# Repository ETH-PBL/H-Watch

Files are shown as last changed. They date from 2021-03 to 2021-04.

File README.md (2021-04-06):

<!--
*** Template source: https://github.com/othneildrew/Best-README-Template/blob/master/README.md
-->

<!-- PROJECT SHIELDS -->
<!--
*** I'm using markdown "reference style" links for readability.
*** Reference links are enclosed in brackets [ ] instead of parentheses ( ).
*** See the bottom of this document for the declaration of the reference variables
*** for contributors-url, forks-url, etc. This is an optional, concise syntax you may use.
*** https://www.markdownguide.org/basic-syntax/#reference-style-links
-->
[][contributors-url]
[][forks-url]
[][stars-url]
[][issues-url]
[][license-url]

<!-- PROJECT LOGO -->
<br />
<p align="center">
  <a href="https://github.com/ETH-PBL/H-Watch">
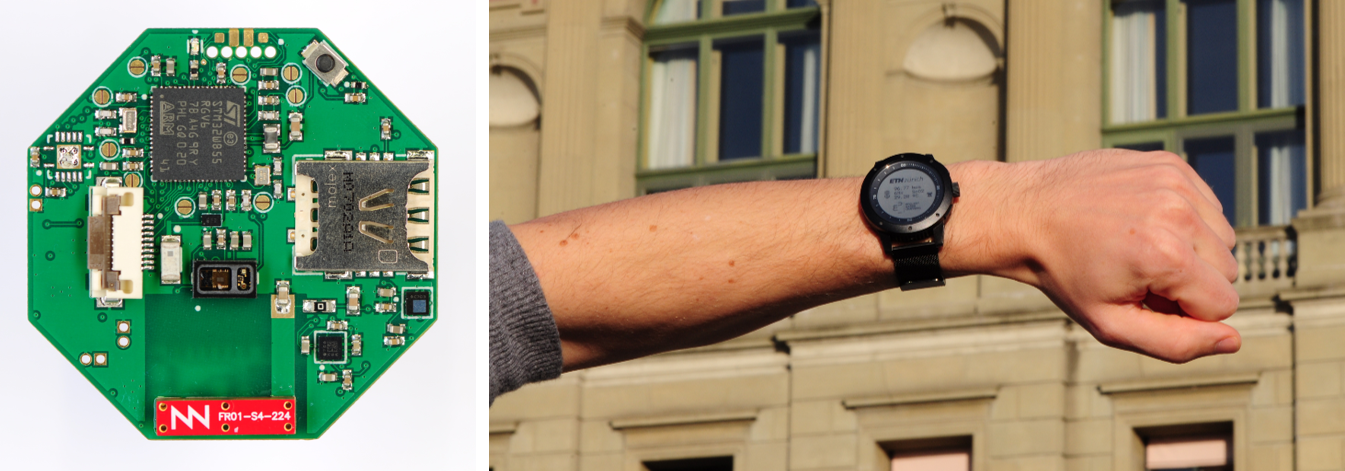
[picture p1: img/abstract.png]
    
  </a>

  <h3 align="center">H-Watch</h3>

  <p align="center">
    Smart Watch for Healthcare
    <br />
    <a href="https://github.com/ETH-PBL/H-Watch"><strong>Explore the docs »</strong></a>
    <br />
    <br />
    <a href="https://www.youtube.com/watch?v=JSp1-hzvBWk">View Demo</a>
    ·
    <a href="https://github.com/ETH-PBL/H-Watch/issues">Report Bug</a>
    ·
    <a href="https://github.com/ETH-PBL/H-Watch/issues">Request Feature</a>
  </p>
</p>

<!-- TABLE OF CONTENTS -->
## Table of Contents

* [About the Project](#about-the-project)
* [Hardware](#hardware)
  * [Components](#hardware)
  * [PCB](#pcb) 
* [Getting Started](#getting-started)
  * [Software](#software)
  * [Installation](#installation)

<!-- ABOUT THE PROJECT -->
## About The Project

The H-Watch is a fully open-sourde wearable long-lasting smart monitoring platform for health monitoring and tracking. Thanks to the integrated state-of-the-art NB-IoT cellular technology, it provides direct and secure cloud connectivity. It  is  based  on  widely  available  off-the-shelf components; however, it is designed with low-power and on-board intelligence in mind. Experimentalresults demonstrated only 5.9 mW of average power consumption, leading to a lifetime of 9 days on a small watch battery wothout, and up to 20 days with the solarenergy harvester.

## Hardware

### Components
The H-Watch is a highly integrated multi-sensor wearable platform which is built of the key components, listed below: 

* [MAX30101EFD+][max301010_url],  High-Sensitivity Pulse Oximeter and Heart-Rate Sensor for Wearable Health
* [LSM303AGR][lsm303agr_url],     Ultra-compact high-performance eCompass module
* [LPS22HB][lps22hb_url],         MEMS nano pressure sensor
* [LSM6DSM][lsm6dsm_url],         Ultra-low power, high accuracy and stability iNEMO 6DoF inertial measurement unit (IMU)
* [MP34DT05-A][mp34dt05_url],     MEMS audio sensor omnidirectional stereo digital microphone
* [BQ25570][bq25570_url],         Ultra Low power Harvester power Management IC with boost charger, and Nanopower Buck Converter
* [STM32WB55RG][stm32wb55_url],   Ultra-low-power dual core Arm Cortex-M4, Cortex-M0+ with 1 Mbyte of Flash memory, Bluetooth LE 5.2
* [BC95GJB-02-STD][bc95G_url],    Multi-band NB-IoT Module with Ultra-low Power Consumption

The H-Watchs housing, as well as its energy-saving memory LCD display, was taken from the [Matrix Power Watch][powerwatch_url] series 1.

### PCB 
The H-Watchs printed circuit board (PCB) is built of 6 Layers with a total board thichness of only 0.83mm. Further informations about the PCB can be found here:

File                                  | Content
--------------------------------------|--------
[H-Watch_schematics.pdf]              | Schematics of the H-Watch.  
[H-Watch_connectors.pdf]              | Description of the position and functionality of all connectors and test pionts.
[H-Watch_assembly.pdf]                | Assembly drawings of the top- and bottom-side of the PCB.
[H-Watch_manufacturing.pdf]           | Detailed fabrication information about the exansion board; thickness, dimensions and defined layer stack.
[H-Watch_layers.pdf]                  | Routing overview of all six copper layers.
[H-Watch_3D.pdf]                      | 3D model of the H-Watches hardware
[H-Watch_complete_documentation.pdf]  | The complete documentation contains all files above, excluding the 3D-PDF

The latest Altium files of of the PCB can be found [here][latest_altium_files]

<!-- GETTING STARTED -->

## Getting Started

* [STM32CubeIDE][stmcubeIDE_url]
* Firmware Package FW_WB V1.8.0

#### Software

### Installation

## Acknowledges
The authors recognise and thank the European Open Science Cloud (EOSC) for financial support under COVID-19 research to open access grant agreements.
EOSCsecretariat.eu has received funding from the European Union's Horizon Programme call H2020-INFRAEOSC-05-2018-2019, grant Agreement number 831644.

If you use **H-Watch** in an academic or industrial context, please cite the following publications:

~~~~
@INPROCEEDINGS{20.500.11850/476189,
	copyright = {Creative Commons Attribution 4.0 International},
	year = {2021-05-22},
	author = {Polonelli, Tommaso and Schulthess, Lukas and Mayer, Philipp and Magno, Michele and Benini, Luca},
	size = {6 p. submitted version},
	keywords = {wearable device; Covid-19; smart sensing; low power design; Tiny Machine Learning; wireless sensor networks},
	language = {en},
	DOI = {10.3929/ethz-b-000476189},
	title = {H-Watch: An Open, Connected Platform for AI-Enhanced COVID19 Infection Symptoms Monitoring and Contact Tracing.},
	Note = {IEEE International Symposium on Circuits and Systems (ISCAS 2021); Conference Location: online; Conference Date: May 22–28}
}
~~~~

<!-- MARKDOWN LINKS & IMAGES -->
<!-- https://www.markdownguide.org/basic-syntax/#reference-style-links -->

<!--Subsection Hardware-->
[max301010_url]:    https://www.maximintegrated.com/en/products/interface/sensor-interface/MAX30101.html
[lsm303agr_url]:    https://www.st.com/en/mems-and-sensors/lsm303agr.html
[lps22hb_url]:      https://www.st.com/en/mems-and-sensors/lps22hb.html
[lsm6dsm_url]:      https://www.st.com/en/mems-and-sensors/lsm6dsm.html
[mp34dt05_url]:     https://www.st.com/en/mems-and-sensors/mp34dt05-a.html
[bq25570_url]:      https://www.ti.com/product/BQ25570
[stm32wb55_url]:    https://www.st.com/en/microcontrollers-microprocessors/stm32wb55rg.html
[bc95G_url]:        https://www.quectel.com/UploadFile/Product/Quectel_BC95-G_NB-IoT_Specification_V1.2.pdf
[powerwatch_url]:   https://www.powerwatch.com/collections/powerwatch/products/black-ops-pack-10  

<!--Subsection PCB-->

[H-Watch_schematics.pdf]:                 /Hardware/H-Watch_V0.2/Documentation/H-Watch_schematics.PDF
[H-Watch_connectors.pdf]:                 /Hardware/H-Watch_V0.2/Documentation/H-Watch_connectors.PDF
[H-Watch_assembly.pdf]:                   /Hardware/H-Watch_V0.2/Documentation/H-Watch_assembly.PDF
[H-Watch_manufacturing.pdf]:              /Hardware/H-Watch_V0.2/Documentation/H-Watch_manufacturing.PDF
[H-Watch_layers.pdf]:                     /Hardware/H-Watch_V0.2/Documentation/H-Watch_layers.PDF
[H-Watch_3D.pdf]:                         /Hardware/H-Watch_V0.2/Documentation/H-Watch_3D.PDF
[H-Watch_complete_documentation.pdf]:     /Hardware/H-Watch_V0.2/Documentation/H-Watch_complete_documentation.PDF
[latest_altium_files]:                    /Hardware/H-Watch_V0.2/   

[stmcubeIDE_url]:	https://www.st.com/en/development-tools/stm32cubeide.html

[contributors-shield]: https://img.shields.io/github/contributors/ETH-PBL/H-Watch.svg?style=flat-square
[contributors-url]: https://github.com/ETH-PBL/H-Watch/graphs/contributors
[forks-shield]: https://img.shields.io/github/forks/ETH-PBL/H-Watch.svg?style=flat-square
[forks-url]: https://github.com/ETH-PBL/H-Watch/network/members
[stars-shield]: https://img.shields.io/github/stars/ETH-PBL/H-Watch.svg?style=flat-square
[stars-url]: https://github.com/ETH-PBL/H-Watch/stargazers
[issues-shield]: https://img.shields.io/github/issues/ETH-PBL/H-Watch.svg?style=flat-square
[issues-url]: https://github.com/ETH-PBL/H-Watch/issues
[license-shield]: https://img.shields.io/github/license/ETH-PBL/H-Watch.svg?style=flat-square
[license-url]: https://github.com/ETH-PBL/H-Watch/blob/master/LICENSE
[product-screenshot]: images/screenshot.png

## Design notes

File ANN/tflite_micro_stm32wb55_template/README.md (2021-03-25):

# STM32CubeIDE template project for STM32WB55 based on TensorFlow Lite micro.

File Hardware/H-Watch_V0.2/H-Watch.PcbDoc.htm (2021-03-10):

Reporting Options

# File in Newer Format

Date | : | 25/09/2020
Time | : | 15:45:50
Filename | : | C:\Users\tommy\OneDrive - Alma Mater Studiorum Università di Bologna\UniBo\SmartCOVID\PrimoPrototipo\SmartWatch\H-Watch.PcbDoc

Version | Warning
Release 20.0 | CAUTION - Support of propagation delay for primitives
Release 20.0 | CAUTION - Support for PCB system parameters, used to contain additional data extracted from components

This file was generated by a later version of the software

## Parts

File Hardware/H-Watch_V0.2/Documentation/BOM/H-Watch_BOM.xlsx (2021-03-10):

Quantity | Designator | Comment | Value | Tolerance | Power | Footprint | Manufacturer | Manufacturer Part Number
1 | R3 | 1M62 | 1620000.00 Ohm | 1 % | 0.1 W | RESC0603(1608)_L
1 | R4 | 7M32 | 7320000.00 Ohm | 1 % | 0.1 W | RESC0603(1608)_L
1 | R5 | 5M49 | 5490000.00 Ohm | 1 % | 0.1 W | RESC0603(1608)_L
2 | R6, R7 | 5M6 | 5600000.00 Ohm | 1 % | 0.1 W | RESC0603(1608)_L
2 | R8, R9 | 10K | 10000.00 Ohm | 1 % | 0.1 W | RESC0603(1608)_L
1 | C7 | 220n |  |  |  | CAPC1005X55X25ML05T10 | Murata
1 | D1 | SML-P11VTT86R |  |  |  | FP-SML-P1-MFG | Rohm | SML-P11VTT86R
1 | J1 | SOIC_Programmer |  |  |  | Programmer
1 | J2 | 52892-1033 |  |  |  | MOLX-52892-1033 | Molex
1 | J12 | 104224-0820 |  |  |  | 1042240820
1 | L1 | 2.2u |  | ±20% |  | INDC2013X140X50LL20T20 | Taiyo Yuden
1 | L2 | CBC3225T220MR | 22uH | 20% |  | INDC1210(3225)X27_L
1 | L3 | 1.5u |  | 20% |  | COILCRAFT-IND-LPS3015
1 | L4 | 6.8u |  | ±30% |  | SUMI-CDRH5D28_V | Sumida
1 | L5 | 10u |  |  |  | MURA-IND0805_L | Murata
1 | R1 | 30k |  |  |  | RESC1005X40X25ML05T05 | Panasonic
1 | R11 | 1.5k |  |  |  | RESC1005X40X25ML05T10 | Yageo / Phycomp
1 | R13 | 0R |  |  |  | RESC1609X55X30ML10T20 | Vishay Dale
1 | SW1 | B3U-1000P |  |  |  | OMRON-B3U-1000_V | Omron Electronic Components
1 | U1 | LSM303AGRTR |  |  |  | FP-LGA-12-8487206-MFG | STMicroelectronics | LSM303AGRTR
1 | U2 | MAX30101EFD+ |  |  |  | FP-F143A5-1-MFG | Maxim Integrated | MAX30101EFD+
1 | U3 | LPS22HBTR |  |  |  | FP-HLGA-10L-8479831-0 | STMicroelectronics | LPS22HBTR
1 | U4 | LSM6DSMTR |  |  |  | FP-LGA-14L-DM00249496-MFG | STMicroelectronics | LSM6DSMTR
1 | U5 | MP34DT05TR-A |  |  |  | FP-HCLGA-DM00231908-MFG | STMicroelectronics | MP34DT05TR-A
1 | U6 | TPS61096ADSST |  |  |  | SON50P200X80_HS-13N | Texas Instruments | TPS61096ADSST
1 | U7 | BQ25570RGRT |  |  |  | QFN50P350X350X100_HS-21L | Texas Instruments
1 | U8 | TPS63031DSKR |  |  |  | DSK10-2000X1200TP_V
1 | U9 | TPS62202DBVT |  |  |  | Z5+1_N
1 | U10 | LM3658SD |  |  |  | SDA10A | National Semiconductor
1 | U11 | STM32WB55RGV6 |  |  |  | FP-VFQFPN-68-B029-MFG | STMicroelectronics | STM32WB55RGV6
1 | U12 | AMCA31-2R450G-S1F-T3 |  |  |  | AMCA31
1 | U13 | MLPF-WB55-01E3 |  |  |  | MLPF-WB55-01E3
1 | U15 | BC95GJB-02-STD |  |  |  | BC95GJB-02-STD | Quectel Wireless Solutions | BC95GJB-02-STD
1 | U16 | FR01-S4-224 |  |  |  | FR01-S4-224 | Fractus Antennas S.L. | FR01-S4-224
1 | U17 | NUP3112UPMUTAG |  |  |  | ONSC-UDFN-6-517AP-01_V | On Semiconductor
1 | Y1 | ABS06-107-32.768KHZ-T |  |  |  | DFN140P200X60-2N-ABS06 | Abracon LLC | ABS06-107-32.768KHZ-T
1 | Y2 | ABM12-32.000MHZ-B2X-T3 |  | 20ppm |  | ABM12
2 | C21, C24 | CAP 4.7uF | 4.7uF | Â±10% |  | CAPC0603(1608)100_L
2 | C22, C25 | CAP 10nF | 10nF | Â±2% |  | CAPC0603(1608)100_L
2 | C32, C33 | CAP 1uF | 1uF | Â±10% |  | CAPC0603(1608)100_L
2 | C37, C38 | 4p |  |  |  | CAPC1005X55X25ML05T10 | Murata
2 | C40, C41 | 8p |  |  |  | CAPC1005X55X25NL05T10 | Murata
2 | C51, C54 | 100p |  |  |  | CAPC1005X56X25ML10T15 | AVX Interconnect / Elco
2 | C57, C58 | NM |  | 10% |  | CAPC1608X90X35ML10T15 | Murata
3 | C20, C30, C39 | 4.7u |  | ±10% |  | CAPC1608X90X20ML10 | TDK
3 | C60, C61, C62 | 33p |  |  |  | CAPC1005X56X25ML10T15 | AVX Interconnect / Elco
3 | R2, R10, R12 | 10k |  | 1% |  | RESC1005X40X25LL05T05 | Panasonic
3 | R14, R15, R16 | 1k |  |  |  | RESC1005X40X25NL05T05 | Vishay Dale
3 | R17, R18, R19 | 22R |  |  |  | RESC1005X40X25LL05T05 | Panasonic
3 | X1, X2, X3 | GRPB012VWVN-RC |  |  |  | Pin Header, 1x2, TH | Sullins Connector Solutions | GRPB012VWVN-RC
5 | C23, C26, C28, C29, C31 | 10u |  |  |  | CAPC1608X90X35NL10T15 | Murata
9 | J3, J4, J5, J6, J7, J8, J9, J10, J11 | Solder Jumper | 1 |  |  | Small Solder Jumper
14 | C1, C3, C5, C8, C9, C10, C12, C14, C16, C18, C42, C44, C46, C48 | 10u |  | ±20% |  | CAPC1005X70X10NL05 | TDK
22 | C2, C4, C6, C11, C13, C15, C17, C19, C27, C34, C35, C36, C43, C45, C47, C49, C50, C52, C53, C55, C56, C59 | 100n |  |  |  | CAPC1005X60X30ML05T10 | Kemet

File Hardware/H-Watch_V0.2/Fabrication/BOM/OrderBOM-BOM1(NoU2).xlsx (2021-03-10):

Name | Description | Designator | Quantity | Manufacturer 1 | Manufacturer Part Number 1 | Manufacturer Lifecycle 1 | Supplier 1 | Supplier Part Number 1 | Supplier Unit Price 1 | Supplier Subtotal 1
BC95GJB-02-STD | NB-IoT Module 54Kbps UART 700MHz to 2100MHz 3.6V Surface Mount | U15 | 1 | Quectel Wireless Solutions | BC95GJB-02-STD | Unknown
SOIC_Programmer |  | J1 | 1
LPS3015-152MRB | INDUCTOR, SHLD, 1.5UH, 20%, 1.3A, SMD | L3 | 1 | Coilcraft | LPS3015-152MRC | Unknown | Coilcraft Direct | LPS3015-152MRC | 0.85971 | 0.85971
5M49 1% 0603(1608) | 5M49 0.1W 1% 0603 (1608 Metric) SMD | R5 | 1 | Vishay | CRCW06035M49FKEA | Volume Production | Digi-Key | 541-5.49MHDKR-ND | 0.0966 | 0.0966
04023A330JAT2A |  | C60, C61, C62 | 3 | Kyocera AVX | 04023A330JAT2A | Volume Production | Digi-Key | 478-12613-6-ND | 0.0966 | 0.28979
04025A101FAT2A. |  | C51, C54 | 2 | Kyocera AVX | 04025A101FAT2A | Volume Production | Digi-Key | 478-3658-6-ND | 0.18353 | 0.36707
104224-0820 | 6 Position Card Connector NANO SIM Surface Mount, Right Angle Gold | J12 | 1 | Molex | 1042240820 | Not Recommended for New Design | Digi-Key | WM23749DKR-ND | 1.27 | 1.27
AMCA31-2R450G-S1F-T3 | Antennas 2.45GHz BW 90dB + Gain -1 dBi avg. | U12 | 1 | Abracon | AMCA31-2R450G-S1F-T3 | Volume Production | Digi-Key | 535-14095-6-ND | 0.51196 | 0.51196
C0402C104K8PACTU |  | C2, C4, C6, C11, C13, C15, C17, C19, C27, C34, C35, C36, C43, C45, C47, C49, C50, C52, C53, C55, C56, C59 | 22 | KEMET | C0402C104K8PACTU | Volume Production | Digi-Key | 399-3027-6-ND | 0.04443 | 0.97756
C1608X5R1C475K080AC | CAP, Ceramic, 4.7 uF, +/- 10%, 16 V, -55 to 85 degC, 0603 (1608 Metric), RoHS, Tape and Reel | C20, C30, C39 | 3 | TDK | C1608X5R1C475K080AC | Volume Production | Digi-Key | 445-7478-6-ND | 0.31877 | 0.95631
CAP 1uF 10V 0603(1608) | CAP 1uF 10V ±10% 0603 (1608 Metric) Thickness 1mm SMD | C32, C33 | 2 | KEMET | C0603C105K8RACTU | Volume Production | Digi-Key | 399-11133-6-ND | 0.0966 | 0.19319
CRCW06030000Z0EA |  | R13 | 1 | Vishay | CRCW0603-0000Z0EA | Volume Production | Digi-Key | 541-0.0GDKR-ND | 0 | 0
ERJ2RKF1002X | Chip Resistor, 10 KOhm, +/- 1%, 0.1 W, -55 to 155 degC, 0402 (1005 Metric), RoHS, Tape and Reel | R2, R10, R12 | 3 | Panasonic | ERJ-2RKF1002X | Volume Production | Digi-Key | P10.0KLDKR-ND | 0.0966 | 0.28979
FR01-S4-224 | 700MHz, 800MHz, 850MHz, 900MHz, 1.7GHz, 1.8GHz, 1.9GHz, 2GHz, 2.1GHz, 2.3GHz, 2.5GHz, 2.6GHz, 3.5GHz, 3.7GHz DCS, GSM, LTE, PCS, UMTS Chip RF Antenna 698MHz ~ 960MHz, 1.71GHz ~ 2.69GHz, 3.4GHz ~ 3.8GHz 1.6dBi, 3.7dBi, 3.1dBi Solder Surface Mount | U16 | 1 | Fractus | FR01-S4-224 | Unknown | Digi-Key | 2115-FR01-S4-224DKR-ND | 2 | 2
GJM1555C1H4R0CB01D |  | C37, C38 | 2 | Murata | GJM1555C1H4R0CB01D | Volume Production | Digi-Key | 490-3098-6-ND | 0.11592 | 0.23183
GRM155R71C224KA12D | Chip Capacitor, 220 nF, +/- 10%, 16 V, -55 to 125 degC, 0402 (1005 Metric), RoHS, Tape and Reel | C7 | 1 | Murata | GRM155R71C224KA12D | Volume Production | Digi-Key | 490-5418-6-ND | 0.13524 | 0.13524
GRPB012VWVN-RC | CONN HEADER 1.27mm Pitch 1x2 POS TH DL PCB AU | X1, X2, X3 | 3 | Sullins | GRPB012VWVN-RC | Obsolete | Digi-Key | S9015E-01-ND | 0 | 0
MP34DT05TR-A | MEMS AUD MIC SENSOR OMNI 4HCLGA | U5 | 1 | STMicroelectronics | MP34DT05TR-A | Unknown | Digi-Key | 497-17809-1-ND | 1.28 | 1.28
NUP3112UPMUTAG | Quad Transient Voltage Suppressor Array, ESD Protection Diodes with Ultra-Low (0.7 pF) Capacitance, 6-Pin UDFN, Pb-Free, Tape and Reel | U17 | 1 | ON Semiconductor | NUP3112UPMUTAG | Volume Production | Digi-Key | NUP3112UPMUTAG-ND | 0.30124 | 903.71
RC0402FR-071K5L |  | R11 | 1 | Yageo | RC0402FR-071K5L | Volume Production | Digi-Key | 311-1.50KLRCT-ND | 0.0966 | 0.0966
STM32WB55RGV6 | ULTRA-LOW-POWER DUAL CORE ARM CO | U11 | 1 | STMicroelectronics | STM32WB55RGV6 | Unknown | Digi-Key | 497-18488-ND | 9.39 | 9.39
TXB0104RGYR | IC TRNSLTR BIDIRECTIONAL 14VQFN | U14 | 1 | Texas Instruments | TXB0104RGYR | Volume Production | Digi-Key | 296-21930-6-ND | 0.98529 | 0.98529
52892-1033 | 0.5 mm Pitch Easy-On(TM) Type FPC Connector, 2.0 mm Mated Height, Right Angle, ZIF, SMT, Bottom Contact, 10 Circuits, -40 to 85 degC, ELV and RoHS Compliant, Tape and Reel | J2 | 1 | Molex | 52892-1033 | Volume Production | Farnell | 2361316 | 0.62836 | 0.62836
C1005X5R0J106M050BC | Chip Capacitor, 10 uF, +/- 20%, -55 to 85 degC, 0402 (1005 Metric), RoHS, Tape and Reel | C1, C3, C5, C8, C9, C10, C12, C14, C16, C18, C42, C44, C46, C48 | 14 | TDK | C1005X5R0J106M050BC | Volume Production | Farnell | 2346872 | 1.11 | 15.51
GRM188R71H104KA93D | Chip Capacitor, 0.1 uF, +/- 10%, 50 V, -55 to 125 degC, 0603 (1608 Metric), RoHS, Tape and Reel | C57, C58 | 2 | Murata | GRM188R71H104KA93D | Volume Production | Farnell | 8820023 | 0.05431 | 0.54306
LM3658SD | Dual Source USB/AC Li Chemistry Charger IC for Portable Applications, 10-pin LLP | U10 | 1 | TI National Semiconductor | LM3658SD | Not Recommended for New Design | Farnell | 1312584 | 1.03 | 1.03
1M62 1% 0603(1608) | 1M62 0.1W 1% 0603 (1608 Metric) SMD | R3 | 1 | Vishay Dale | CRCW06031M62FKEB | Volume Production | Mouser | 71-CRCW06031M62FKEB | 0.0966 | 0.0966
5M6 1% 0603(1608) | 5M6 0.1W 1% 0603 (1608 Metric) SMD | R6, R7 | 2 | Vishay | CRCW06035M60FKEA | Volume Production | Mouser | 71-CRCW06035M60FKEA | 0.0966 | 0.19319
7M32 1% 0603(1608) | 7M32 0.1W 1% 0603 (1608 Metric) SMD | R4 | 1 | Vishay | CRCW06037M32FKEA | Not Recommended for New Design | Mouser | 71-CRCW06037M32FKEA | 0.0966 | 0.0966
10K 1% 0603(1608) | 10K 0.1W 1% 0603 (1608 Metric) SMD | R8, R9 | 2 | Bourns | CR0603-FX-1002ELF | Volume Production | Mouser | 652-CR0603FX-1002ELF | 0.00676 | 0.06762
ABM12-32.000MHZ-B2X-T3 | 32MHz ±20ppm Crystal 8pF 200 Ohm -20°C ~ 70°C Surface Mount 4-SMD, No Lead (DFN, LCC) | Y2 | 1 | Abracon | ABM12-32.000MHZ-B2X-T3 | Volume Production | Mouser | 815-ABM12-32-B2XT3 | 1.8 | 1.8
ABS06-107-32.768KHZ-T | CRYSTAL 32.7680KHZ 4PF SMD | Y1 | 1 | Abracon | ABS06-107-32.768KHZ-T | Volume Production | Mouser | 815-ABS06-107-32.7-T | 1.15 | 1.15
B3U-1000P | Ultra-Small Tactile Switch, 0.05 A, 12 V, -25 to 70 degC, 2-Pin SMD, RoHS, Tape and Reel | SW1 | 1 | Omron | B3U-1000P | Volume Production | Mouser | 653-B3U-1000P | 0.91767 | 0.91767
BRC2012T2R2MD | Wire-Wound Chip Power Inductor, 2.2 uH, +/- 20%, -40 to 105 degC, 2-Pin SMD (0805), RoHS, Tape and Reel | L1 | 1 | Taiyo Yuden | BRC2012T2R2MD | Volume Production | Mouser | 963-BRC2012T2R2MD | 0.32843 | 0.32843
CAP 4.7uF 10V 0603(1608) | CAP 4.7uF 10V ±10% 0603 (1608 Metric) Thickness 1mm SMD | C21, C24 | 2 | Yageo | CC0603KRX5R6BB475 | Volume Production | Mouser | 603-CC603KRX5R6BB475 | 0.22217 | 0.44435
CAP 10nF 10V 0603(1608) | CAP 10nF 10V ±2% 0603 (1608 Metric) Thickness 1mm SMD | C22, C25 | 2 | KEMET | C0603C103G8GACTU | Volume Production | Mouser | 80-C0603C103G8GACTU | 0.77278 | 1.55
CBC3225T220MR | FIXED IND 22UH 780MA 351 MOHM | L2 | 1 | Taiyo Yuden | CBC3225T220MR | Volume Production | Mouser | 963-CBC3225T220MR | 0.26081 | 0.26081
CDRH5D28NP-6R2NC | Power Inductor, 6.2 uH, +/- 30%, 1.8 A, -40 to 100 degC, 2-Pin SMD, RoHS, Tape and Reel | L4 | 1 | Sumida | CDRH5D28NP-6R2NC | Volume Production | Mouser | 851-CDRH5D28NP-6R2NC | 0.66652 | 0.66652
CRCW04021K00FKED |  | R14, R15, R16 | 3 | Vishay Dale | CRCW04021K00FKED | Volume Production | Mouser | 71-CRCW0402-1.0K-E3 | 0.0966 | 0.28979
ERJ2RKF22R0X |  | R17, R18, R19 | 3 | Panasonic | ERJ-2RKF22R0X | Volume Production | Mouser | 667-ERJ-2RKF22R0X | 0.0966 | 0.28979
ERJ-2RKF3002X |  | R1 | 1 | Panasonic | ERJ-2RKF3002X | Volume Production | Mouser | 667-ERJ-2RKF3002X | 0.0966 | 0.0966
GJM1555C1H8R0CB01D |  | C40, C41 | 2 | Murata | GJM1555C1H8R0CB01D | Volume Production | Mouser | 81-GJM1555C1H8R0CB01 | 0.11592 | 0.23183
GRM188R60J106ME47D |  | C23, C26, C28, C29, C31 | 5 | Murata | GRM188R60J106ME47D | Volume Production | Mouser | 81-GRM188R60J106ME47 | 0.35741 | 1.79
LPS22HBTR | MEMS NANO PRESSURE SENSOR: 260-1 | U3 | 1 | STMicroelectronics | LPS22HBTR | Volume Production | Mouser | 511-LPS22HBTR | 2.55 | 2.55
LQM21FN100M70L | Fixed Inductor, 10 uH, +/-20%, -55 to 125 degC, 2-Pin SMD (0805), RoHS, Tape and Reel | L5 | 1 | Murata | LQM21FN100M70L | Volume Production | Mouser | 81-LQM21FN100M70L | 0.19319 | 0.19319
LSM6DSMTR | IMU ACCEL/GYRO I2C/SPI 14LGA | U4 | 1 | STMicroelectronics | LSM6DSMTR | Not Recommended for New Design | Mouser | 511-LSM6DSMTR | 2.81 | 2.81
LSM303AGRTR | IMU ACCEL/MAG I2C/SPI 12LGA | U1 | 1 | STMicroelectronics | LSM303AGRTR | New Product | Mouser | 511-LSM303AGRTR | 2.56 | 2.56
MLPF-WB55-01E3 | Prices include import duty and tax. RF FILTER, 2.4GHZ TO 2.5GHZ, WLCSP-6; | U13 | 1 | STMicroelectronics | MLPF-WB55-01E3 | Unknown | Mouser | 511-MLPF-WB55-01E3 | 0.31877 | 0.31877
SML-P11VTT86R | LED RED CLEAR 1006 SMD | D1 | 1 | Rohm | SML-P11VTT86R | Volume Production | Mouser | 755-SML-P11VTT86R | 0.36707 | 0.36707
BQ25570RGRT | IC ENERGY HARV CTRLR BATT 20VQFN | U7 | 1 | Texas Instruments | BQ25570RGRT | Volume Production | TI store | BQ25570RGRT | 5.76 | 5.76
TPS61096ADSST | Boost Switching Regulator IC Positive Fixed 3.3V, - 2 Output 350mA (Switch) 6-WFDFN | U6 | 1 | Texas Instruments | TPS61096ADSST | Unknown | TI store | TPS61096ADSST | 1.75 | 1.75
TPS62202DBVT | Buck Switching Regulator IC Positive Fixed 1.8V 1 Output 300mA SOT-23 | U9 | 1 | Texas Instruments | TPS62202DBVR | Volume Production | TI store | TPS62202DBVR | 0.78244 | 0.78244
TPS63031DSKR | Buck-Boost Switching Regulator IC Positive Fixed 3.3V 1 Output 900mA (Switch) 10-WFDFN Exposed Pad | U8 | 1 | Texas Instruments | TPS63031DSKR | Volume Production | TI store | TPS63031DSKR | 1.37 | 1.37

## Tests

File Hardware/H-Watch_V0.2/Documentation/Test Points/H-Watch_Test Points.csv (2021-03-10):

Net | Name | X Coord | Y Coord | Side | Hole Size | Type

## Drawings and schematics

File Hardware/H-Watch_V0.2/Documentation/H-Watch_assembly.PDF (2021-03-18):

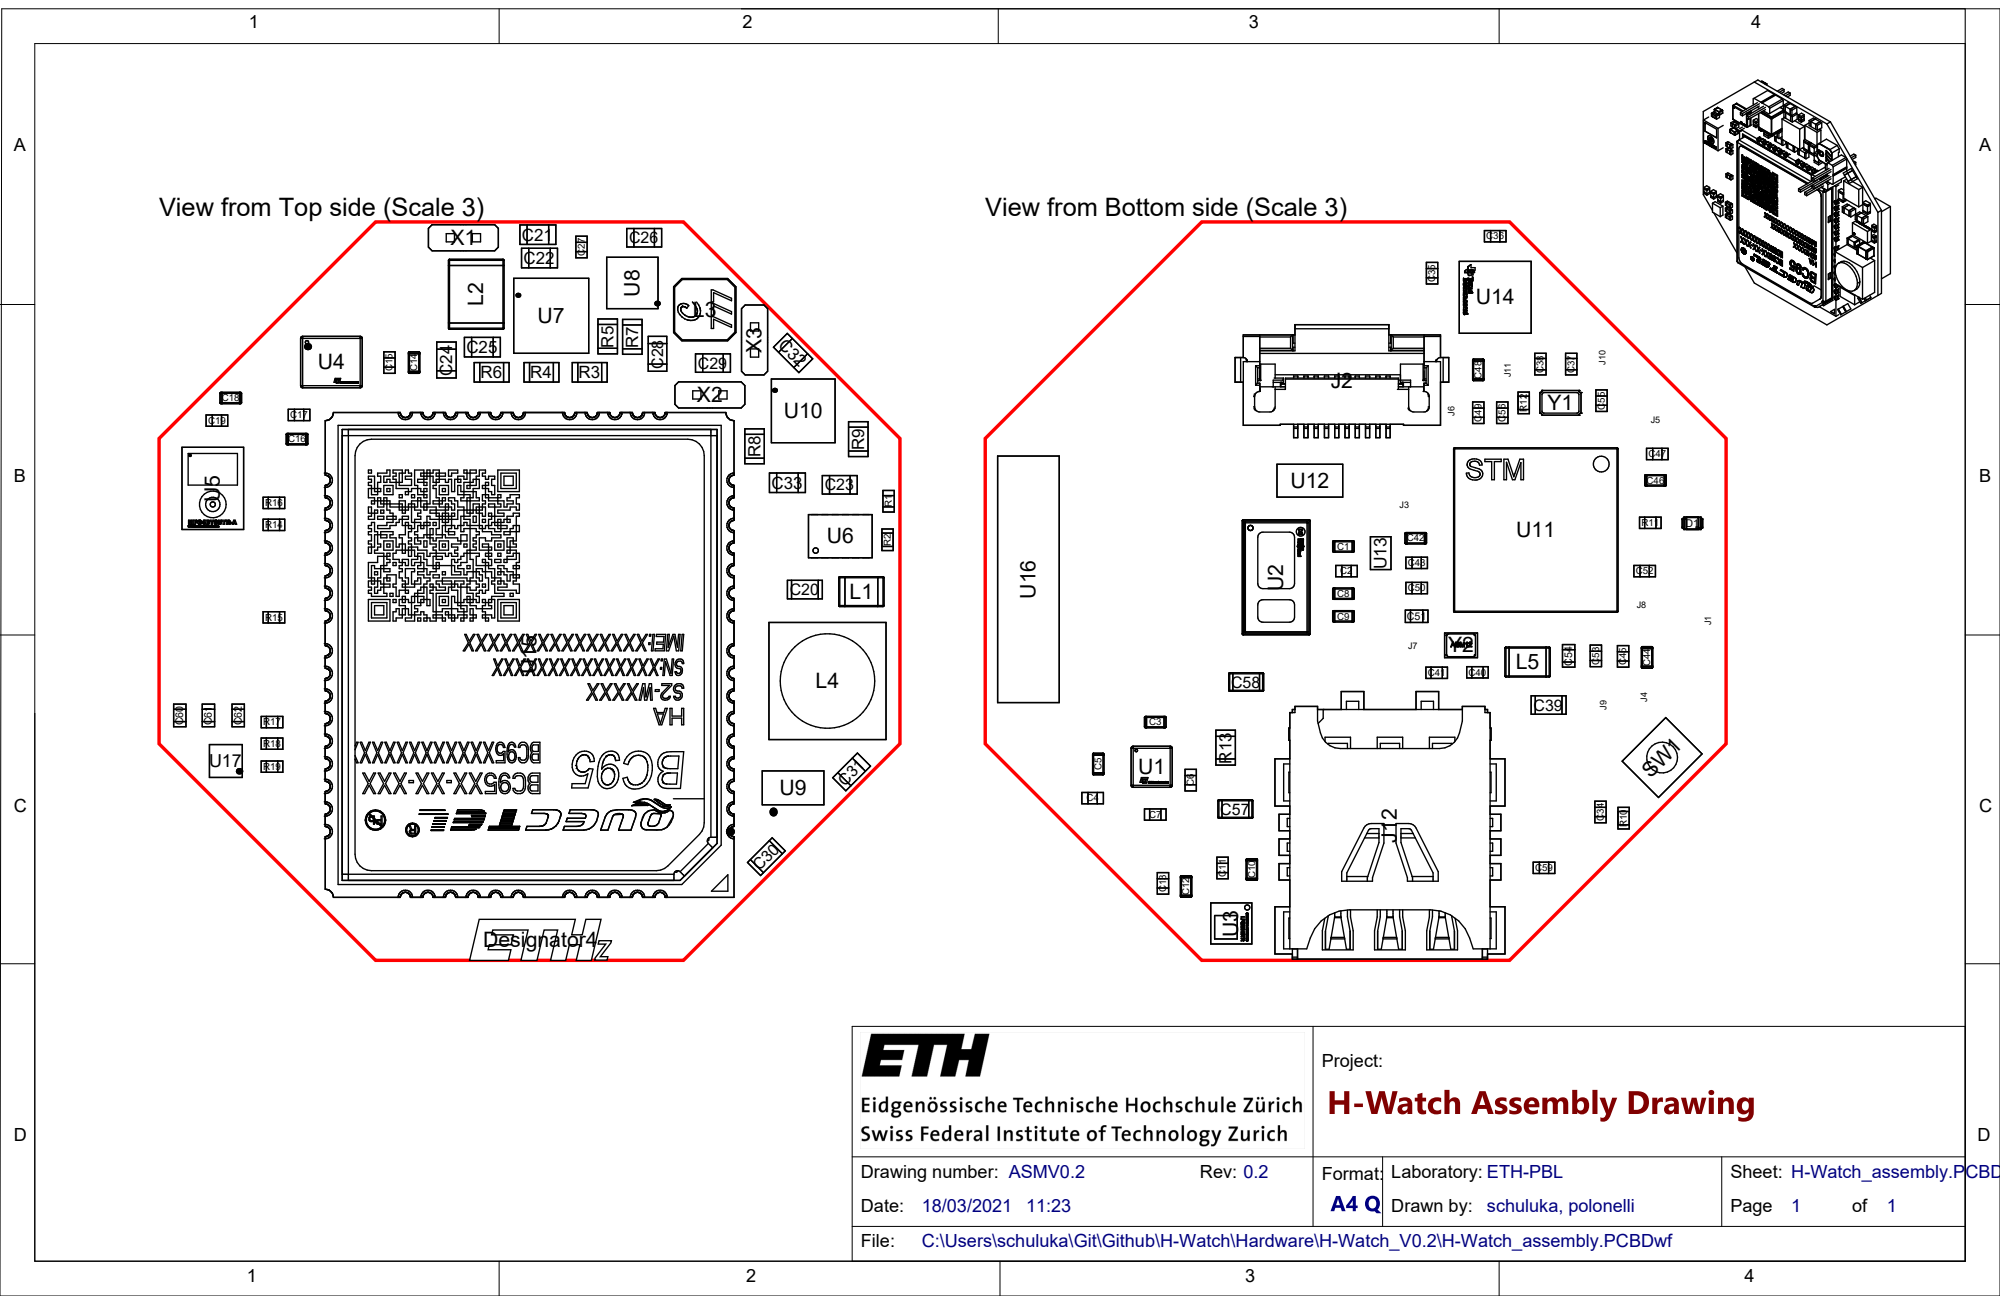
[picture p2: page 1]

View from Top side (Scale 3)

View from Bottom side (Scale 3)

C:\Users\schuluka\Git\Github\H-Watch\Hardware\H-Watch_V0.2\H-Watch_assembly.PCBDwf

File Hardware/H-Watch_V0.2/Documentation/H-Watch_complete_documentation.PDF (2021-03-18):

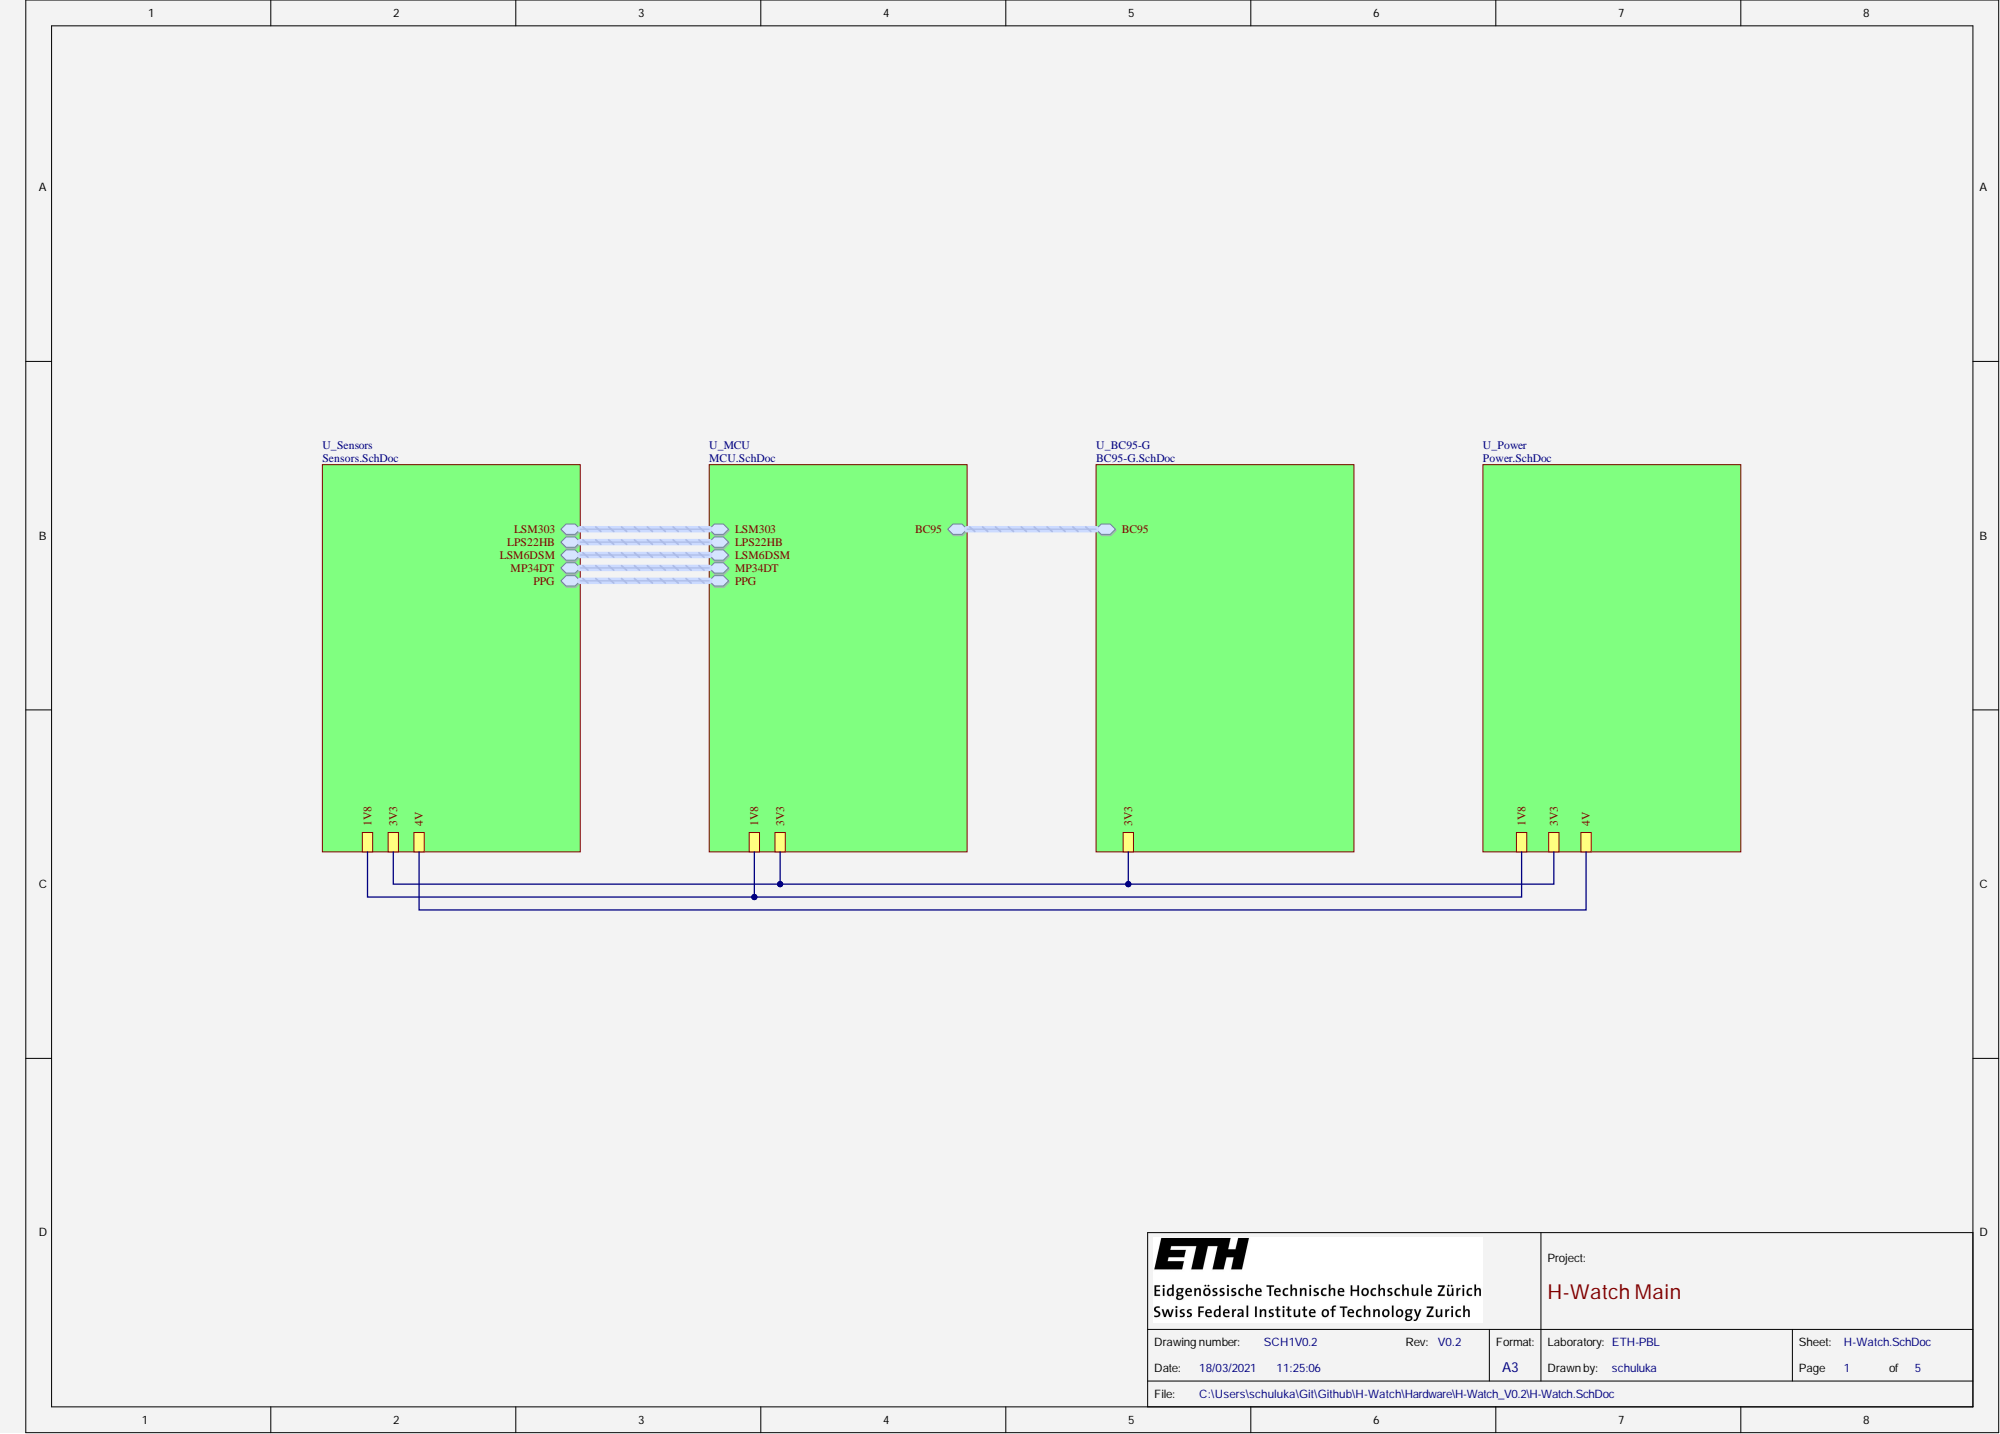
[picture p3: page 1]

Project: H-Watch Main

Drawing number: SCH1V0.2 Rev: V0.2 Date: 11:25:06 | Format: A3 | Laboratory: ETH-PBL Drawn by: schuluka | Sheet: H-Watch.SchDoc Page 1 of 5

C:\Users\schuluka\Git\Github\H-Watch\Hardware\H-Watch_V0.2\H-Watch.SchDoc

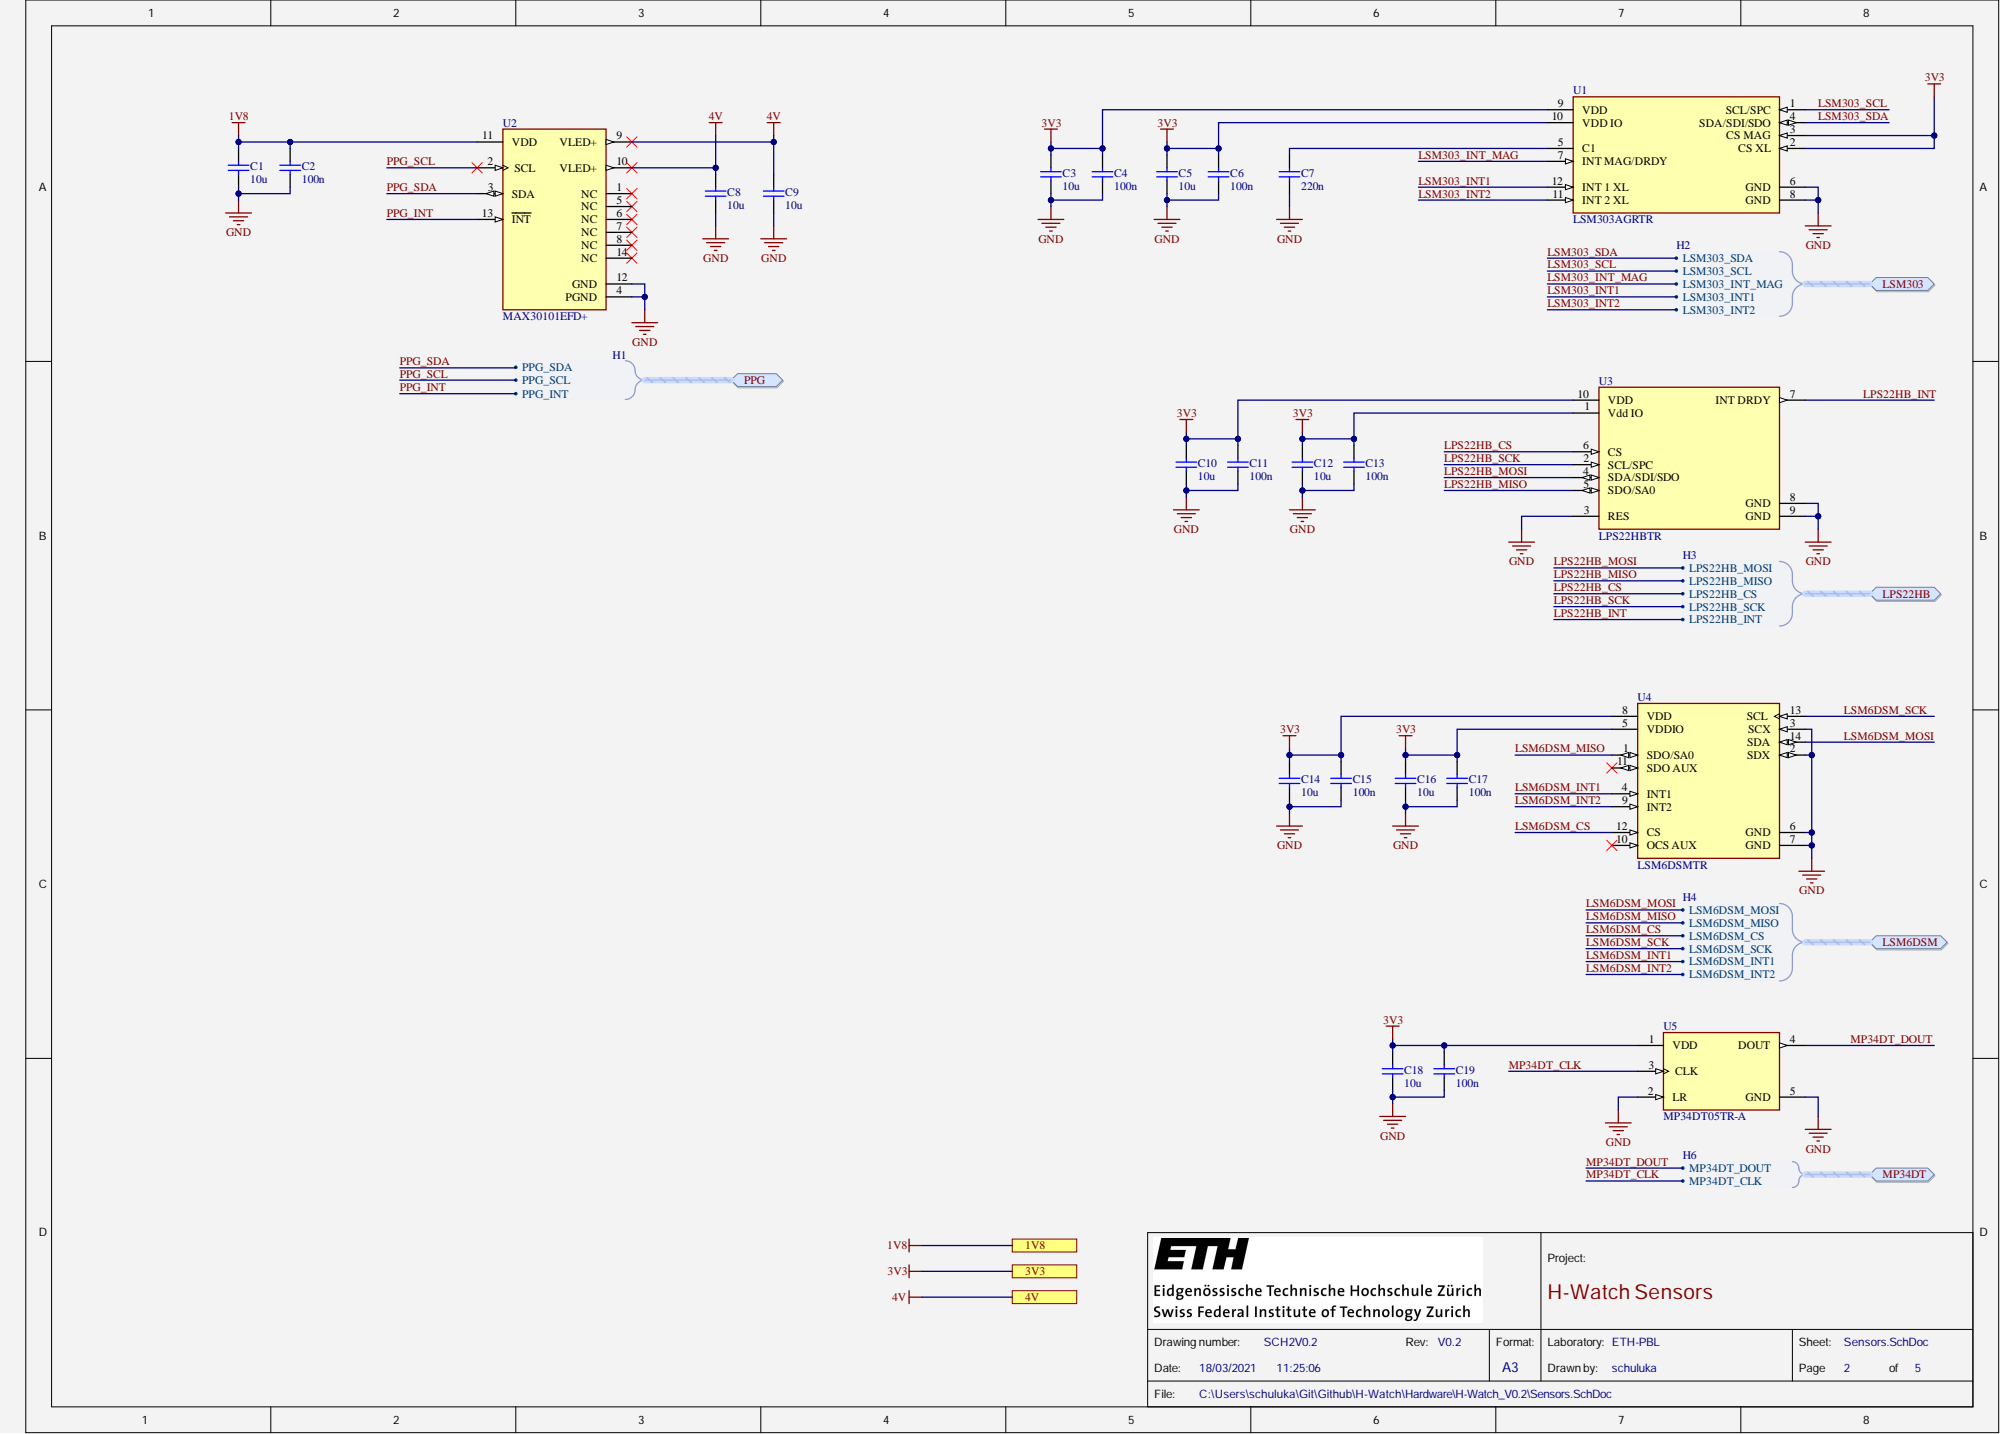
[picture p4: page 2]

Project: H-Watch Sensors

Drawing number: SCH2V0.2 Rev: V0.2 11:25:06 | Format: A3 | Laboratory: ETH-PBL schuluka | Sheet: Sensors.SchDoc Page 2 of 5

C:\Users\schuluka\Git\Github\H-Watch\Hardware\H-Watch_V0.2\Sensors.SchDoc

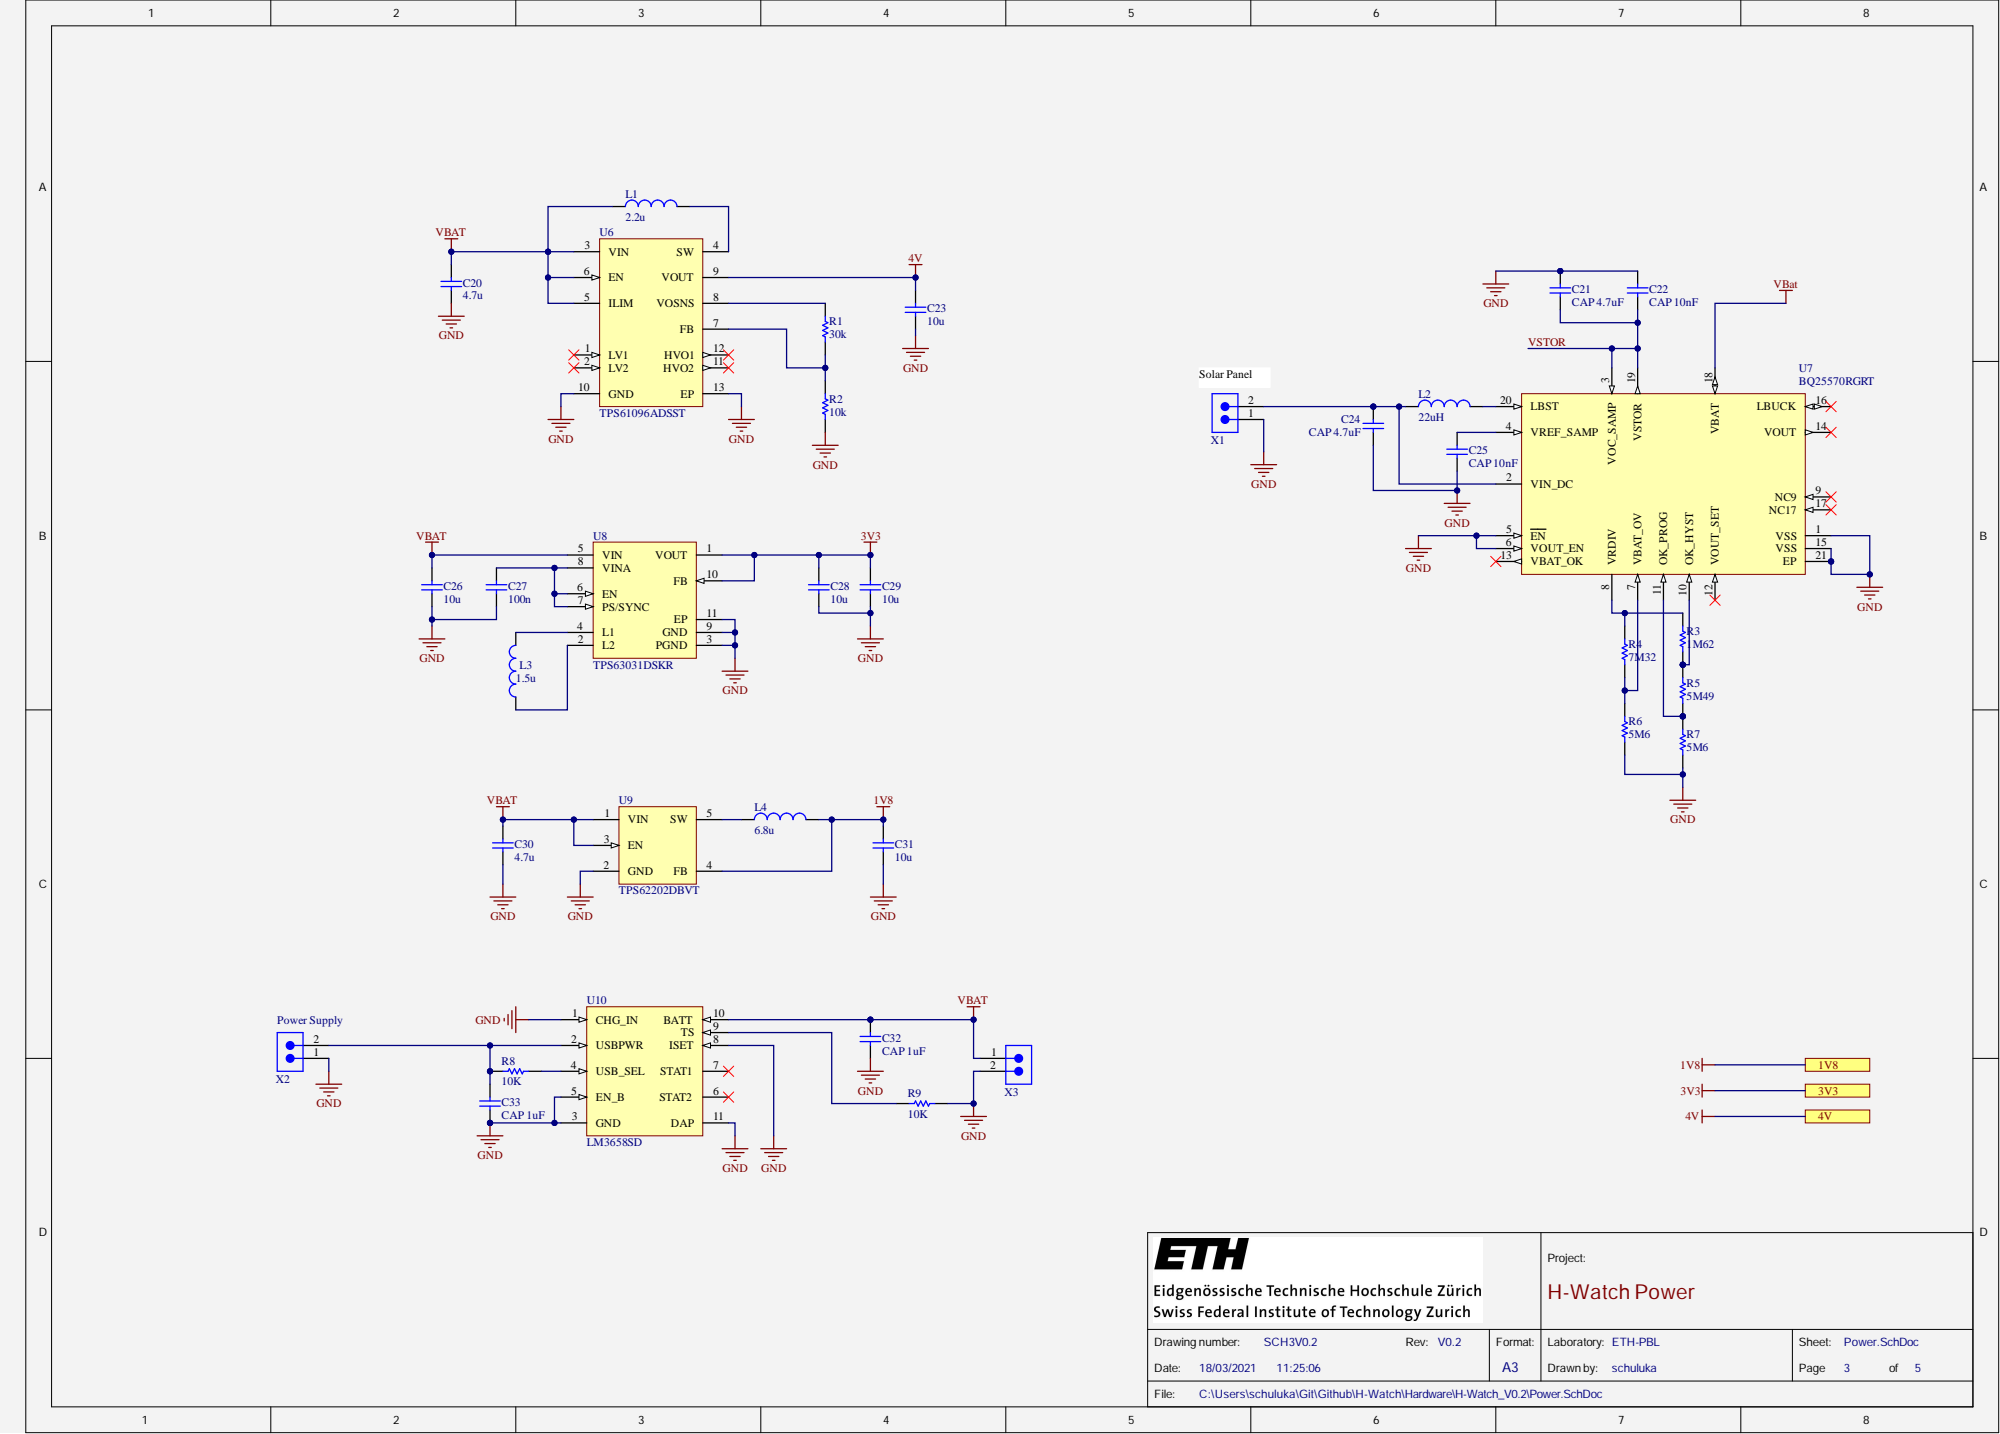
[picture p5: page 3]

Proje c t: H -W a tc h P o we r

Drawing num b e r: SC H 3V 0. 2 R e v : V0. 2 D a te : 1 : 06 | Form a t: A 3 | Laborato ry : ET H -P B L Drawn by : s chul u k a | Shee t: Power. S c h D o c Pag e 3 of 5

chuluka\Git\Github\H-Watch\H

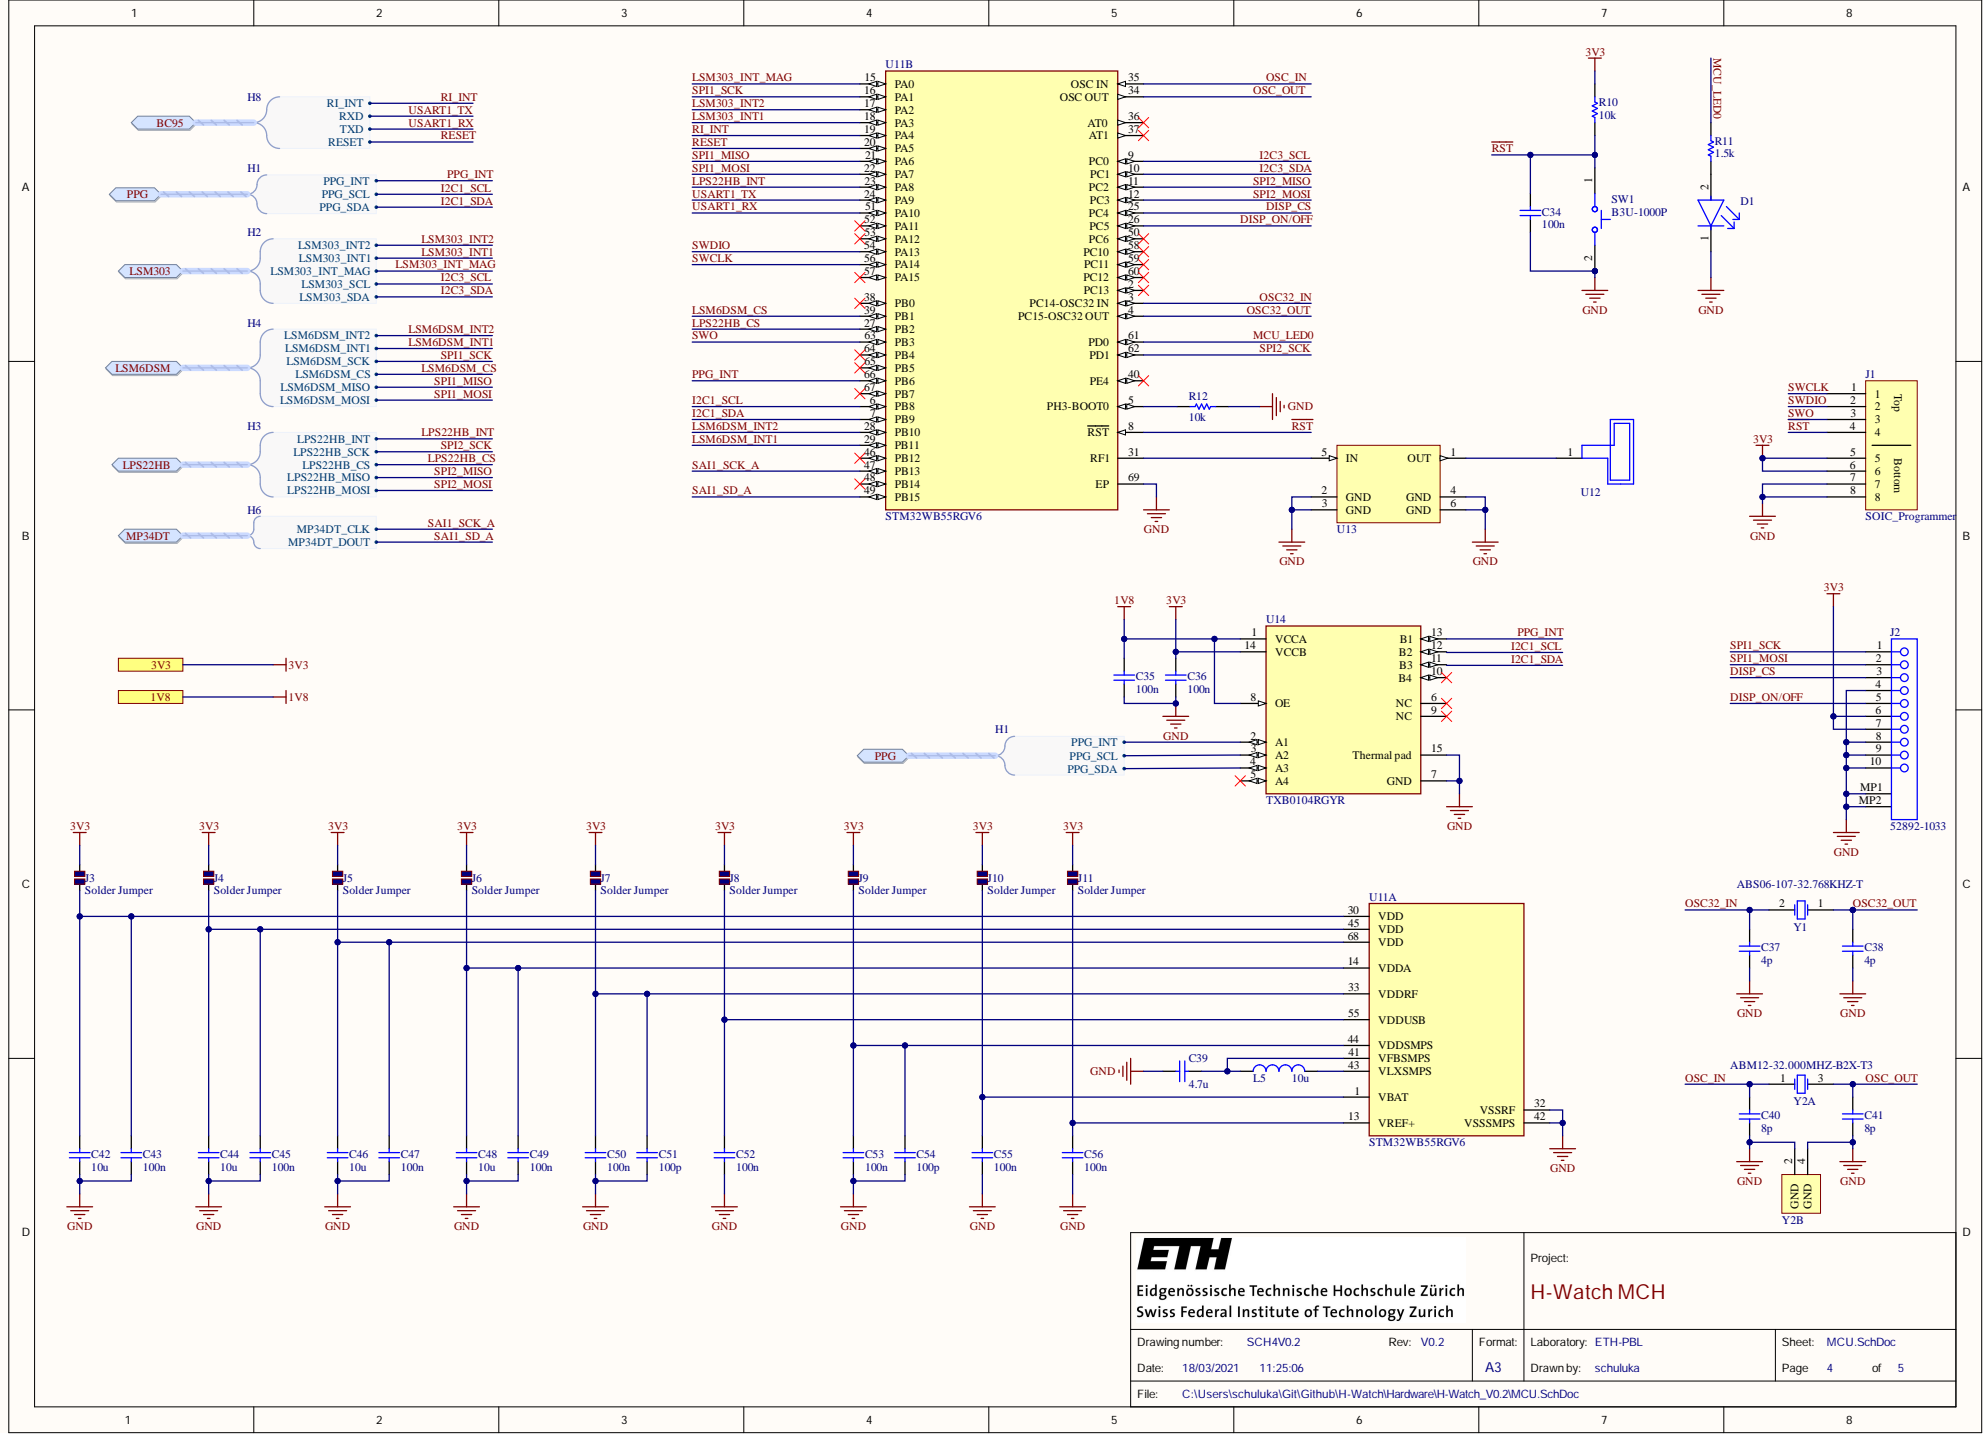
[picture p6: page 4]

6 6
7 7

VDD 68

VDDRF 33

VDDSMPS 44
VFBSMPS 41

Project: H-Watch MCH

Drawing number: SCH4V0.2 Rev: V0.2 11:25:06 | Format: A3 | Laboratory: ETH-PBL schuluka | Sheet: MCU.SchDoc Page 4 of 5

C:\Users\schuluka\Git\Github\H-Watch\Hardware\H-Watch_V0.2\MCU.SchDoc

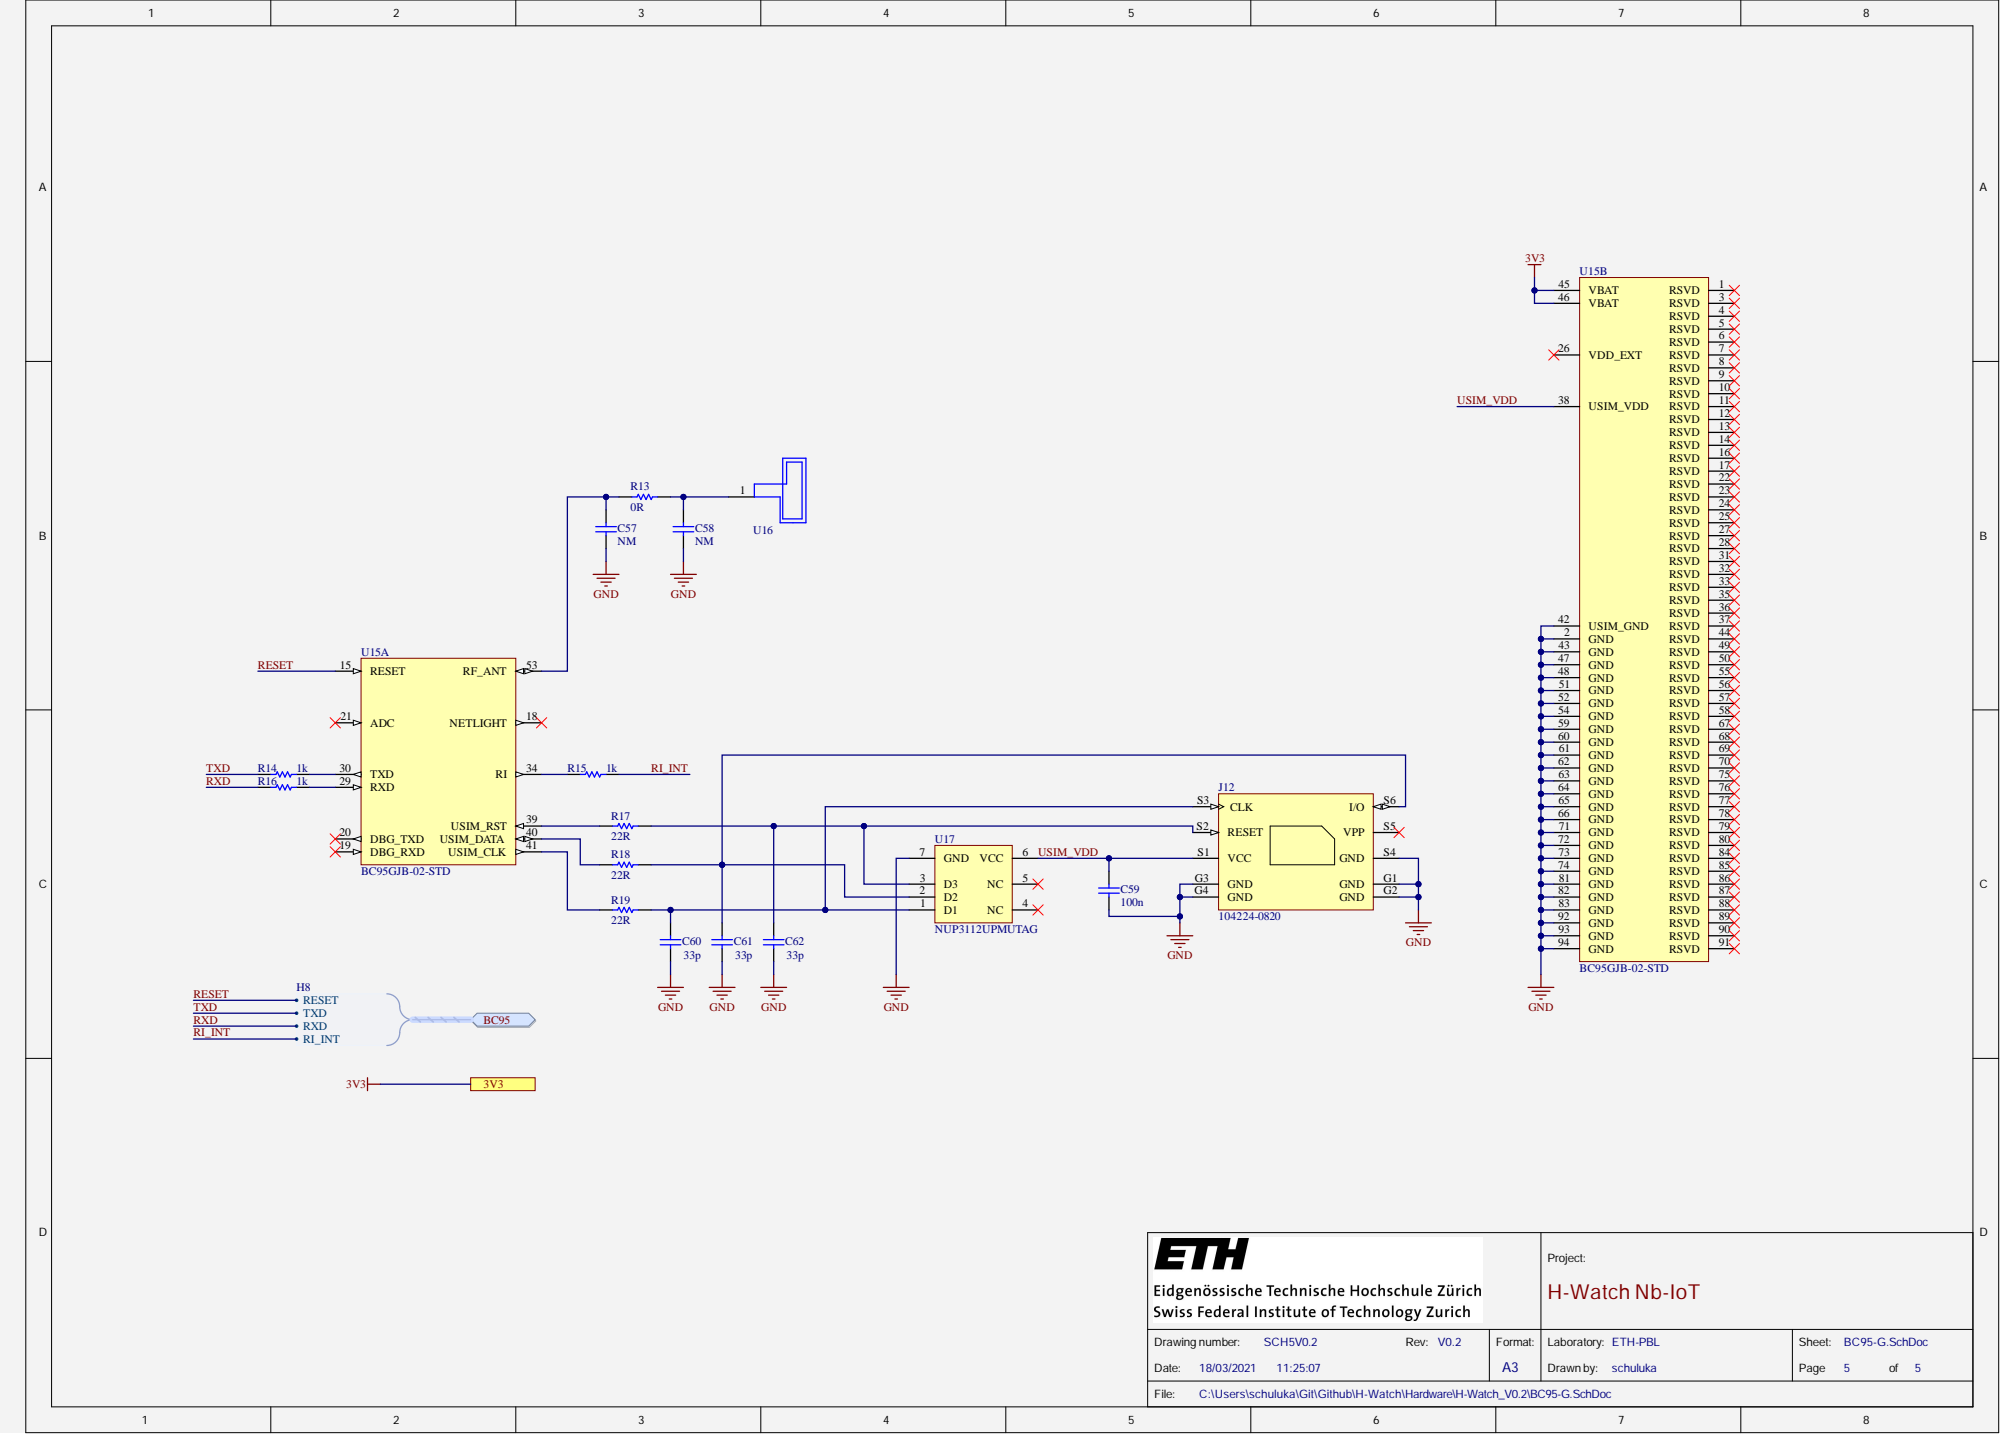
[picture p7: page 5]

Proje c t: H -W a tc h N b -I o T

Drawing num b e r: SC H 5V 0. 2 R e v : V0. 2 D a te : 1 : 07 | Form a t: A 3 | Laborato ry : ET H -P B L Drawn by : s chul u k a | Shee t: BC95-G. S c h D o c Pag e 5 of 5

chuluka\Git\Github\H-Watch\H

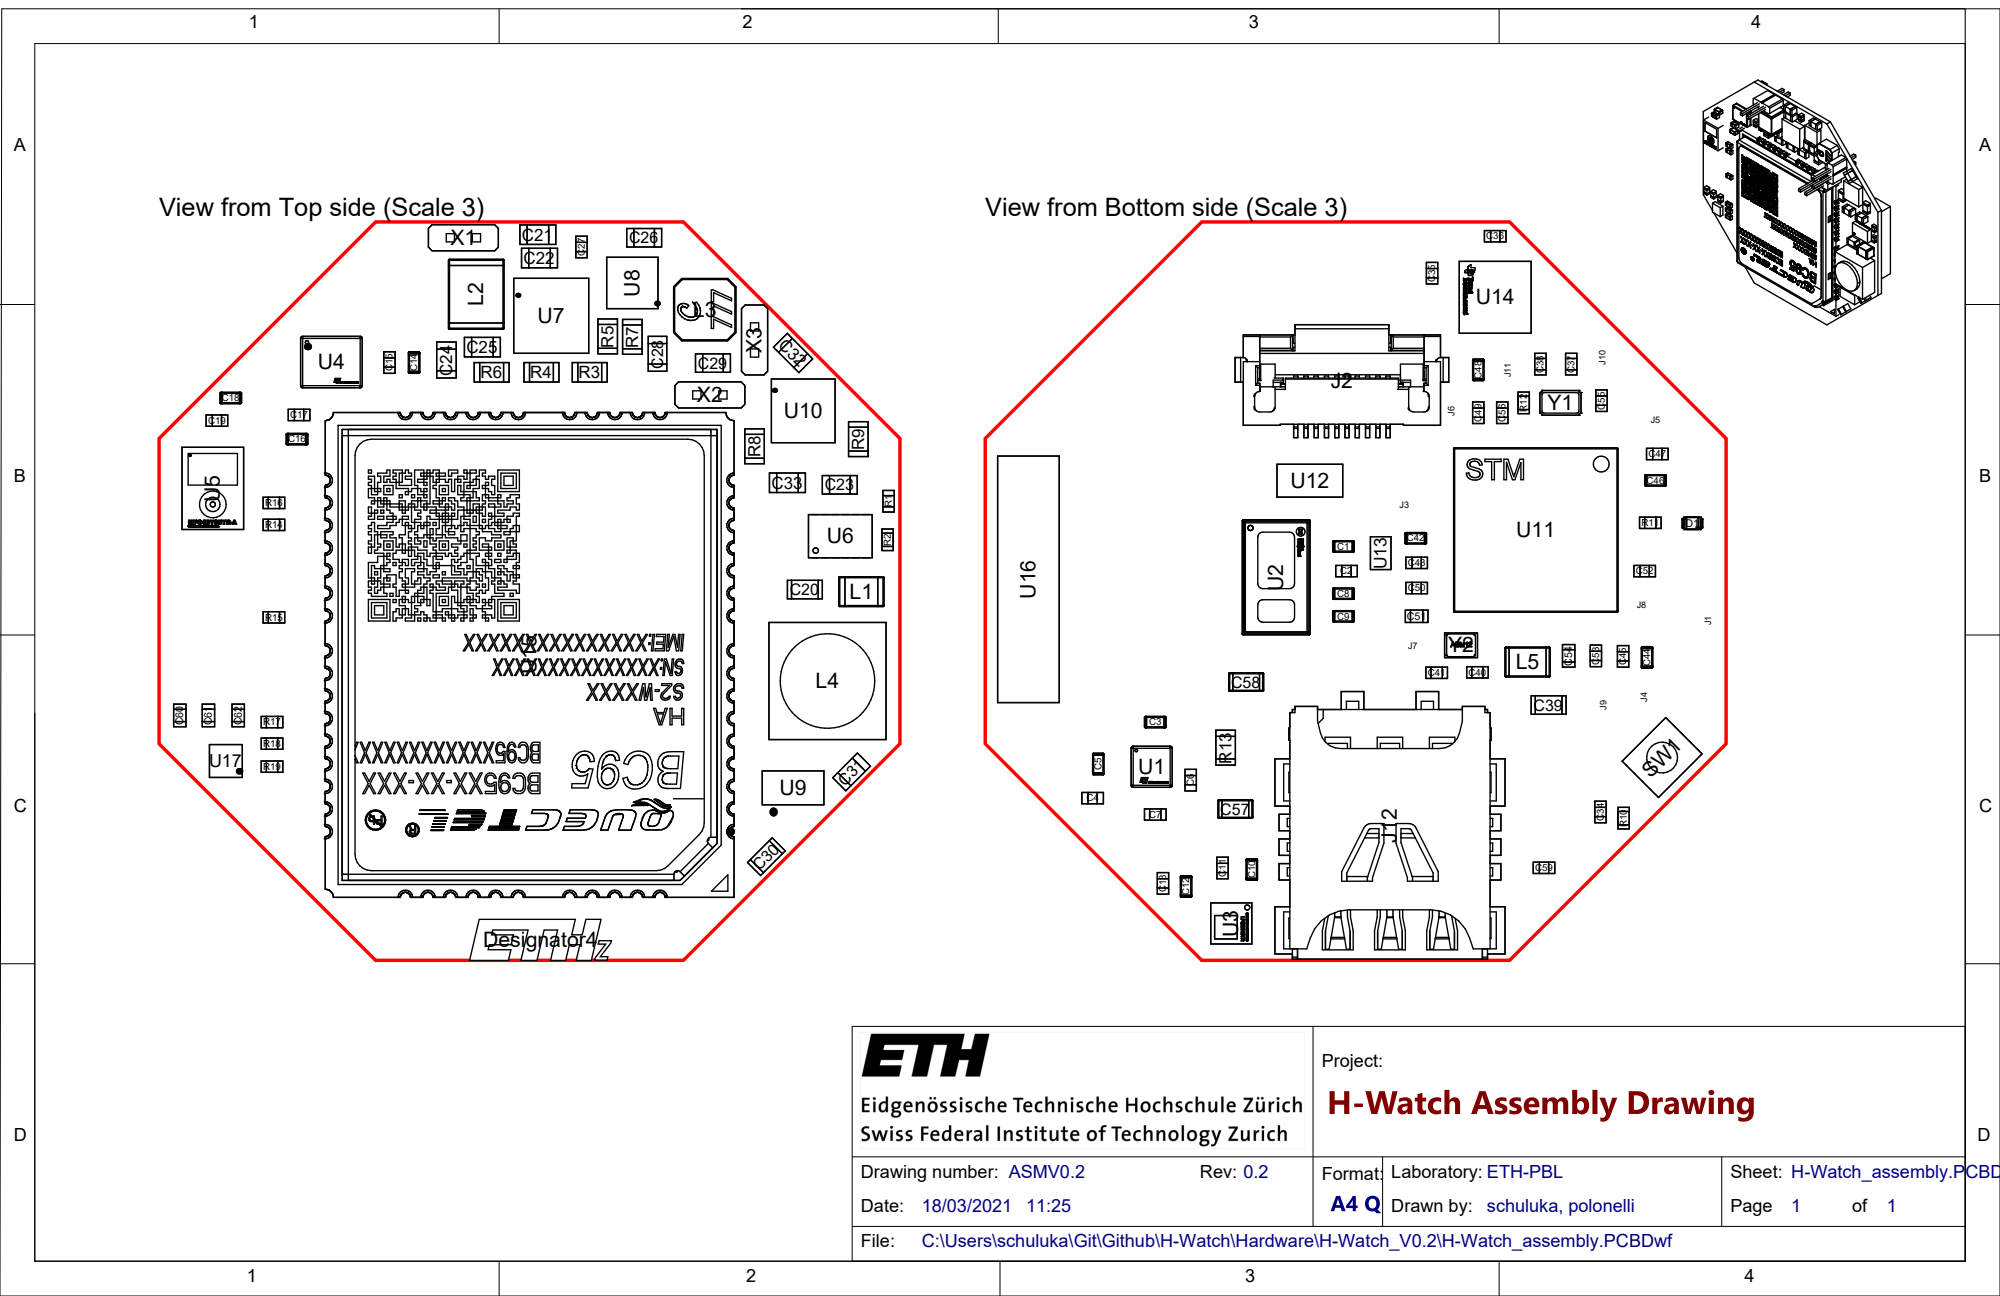
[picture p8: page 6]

View from Top side (Scale 3)

View from Bottom side (Scale 3)

C:\Users\schuluka\Git\Github\H-Watch\Hardware\H-Watch_V0.2\H-Watch_assembly.PCBDwf

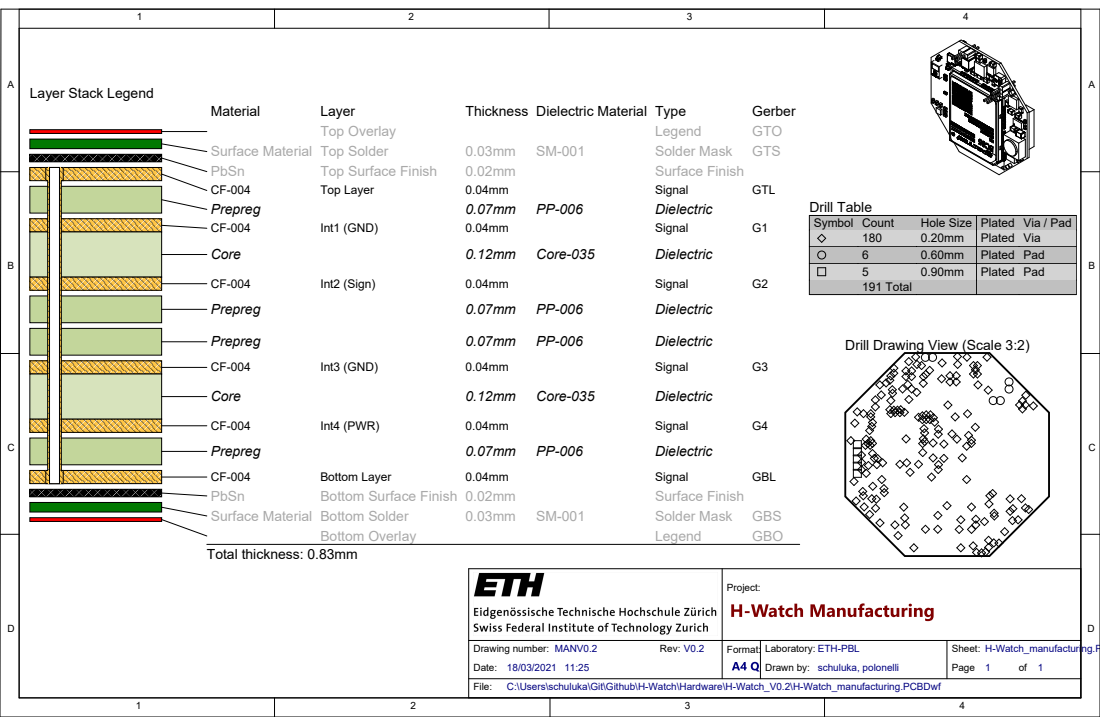
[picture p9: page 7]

Symbol | Count | Hole Size | Plated | Via / Pad

180 | 0.20mm | Plated | Via
6 | 0.60mm | Plated | Pad
5 | 0.90mm | Plated | Pad
191 Total

Drill Drawing View (Scale 3:2)

C:\Users\schuluka\Git\Github\H-Watch\Hardware\H-Watch_V0.2\H-Watch_manufacturing.PCBDwf

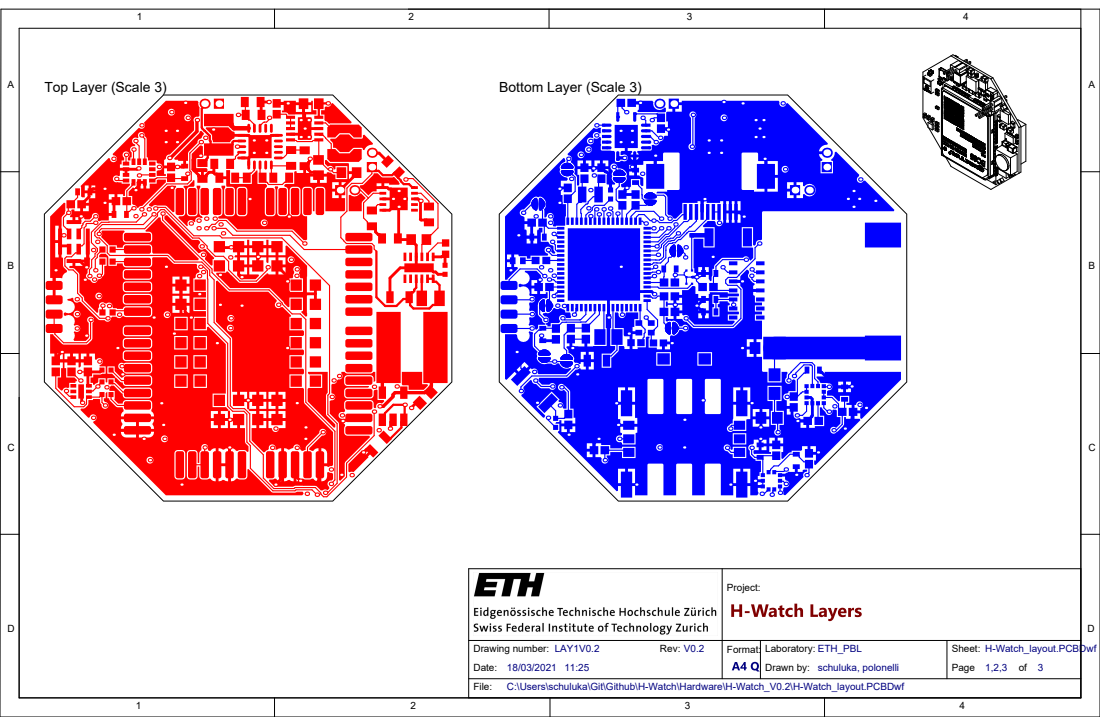
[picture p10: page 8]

Project:

Drawing number: LAY1V0.2 Rev: V0.2 | Format: | Laboratory: ETH_PBL | Sheet: H-Watch_layout.PCBDwf Page 1,2,3 of 3

C:\Users\schuluka\Git\Github\H-Watch\Hardware\H-Watch_V0.2\H-Watch_layout.PCBDwf

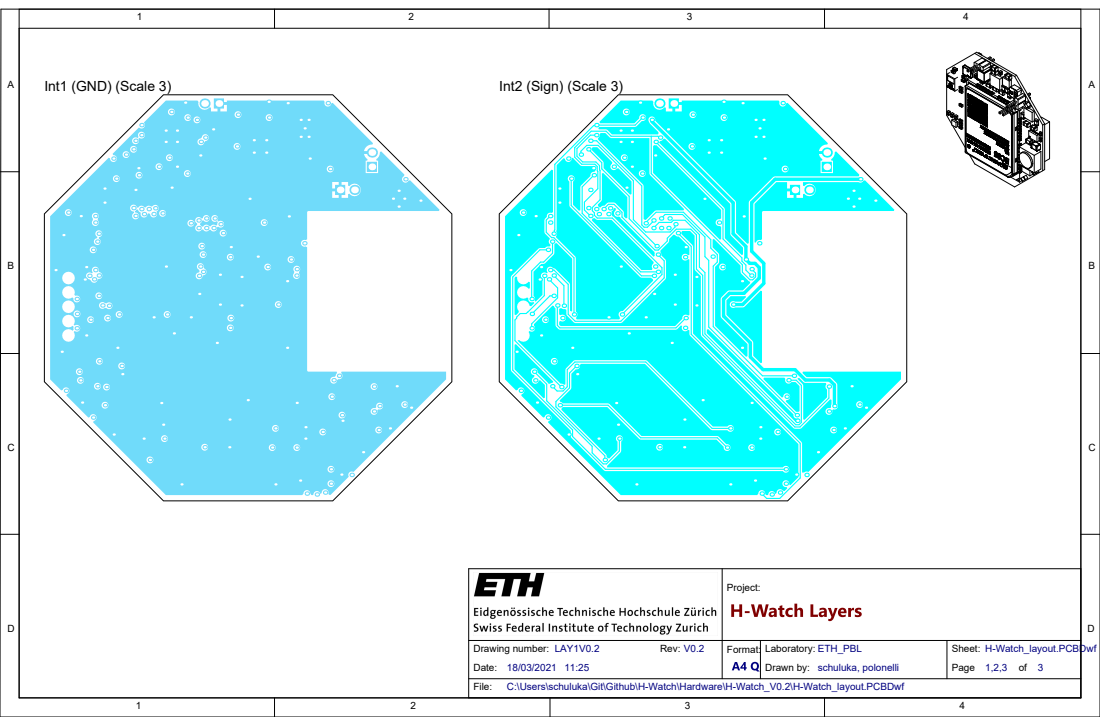
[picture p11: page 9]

Project:

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

C:\Users\schuluka\Git\Github\H-Watch\Hardware\H-Watch_V0.2\H-Watch_layout.PCBDwf

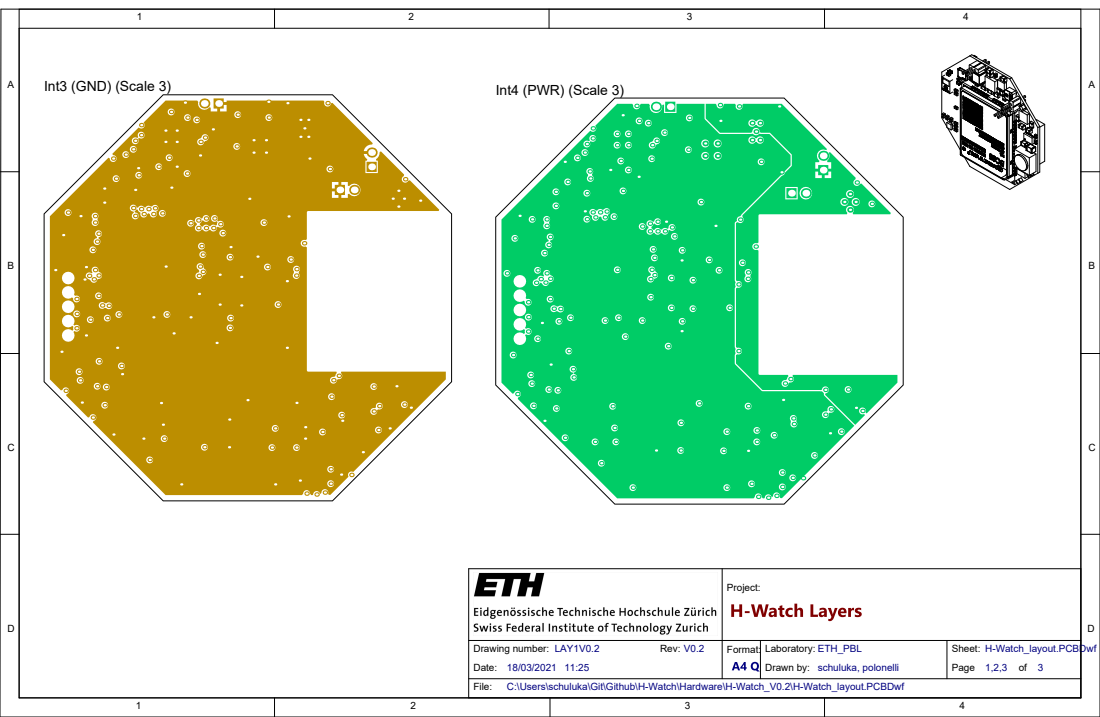
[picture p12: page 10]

Project:

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

C:\Users\schuluka\Git\Github\H-Watch\Hardware\H-Watch_V0.2\H-Watch_layout.PCBDwf

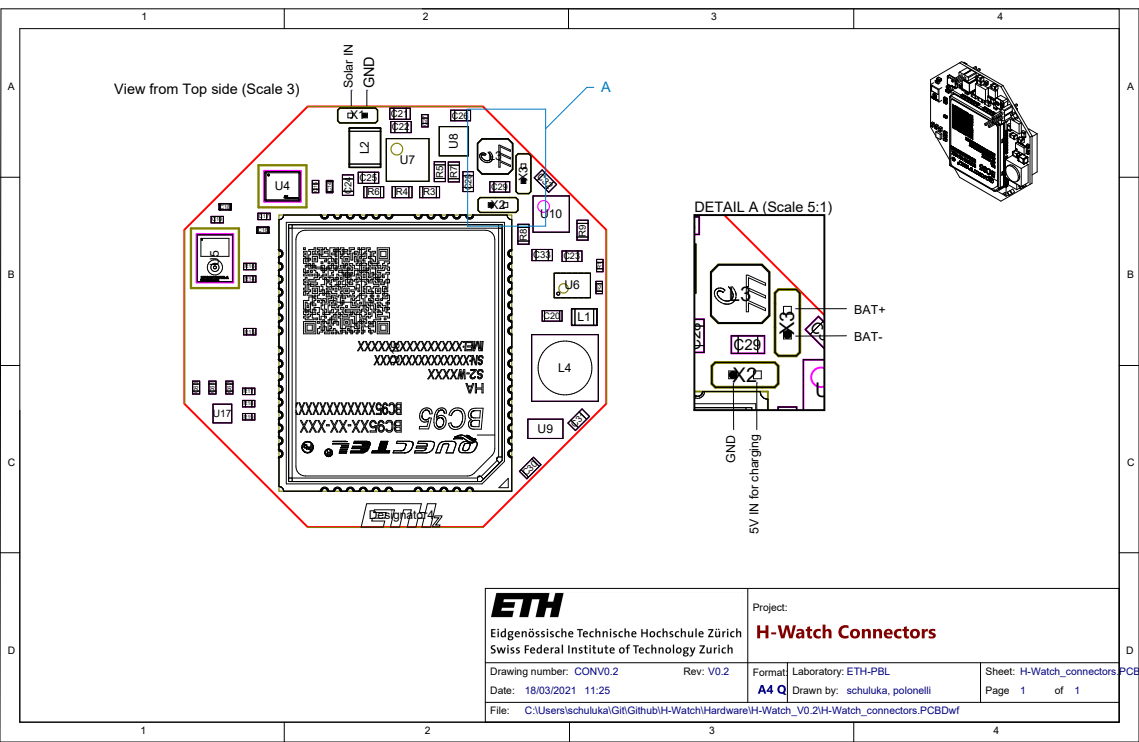
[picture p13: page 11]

Solar IN
DETAIL A (Scale 5:1) GND 5V IN for charging

C:\Users\schuluka\Git\Github\H-Watch\Hardware\H-Watch_V0.2\H-Watch_connectors.PCBDwf

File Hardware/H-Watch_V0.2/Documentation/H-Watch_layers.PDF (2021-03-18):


Project:

Drawing number: LAY1V0.2 Rev: V0.2 Date: | Format: | Laboratory: ETH_PBL Drawn by: schuluka, polonelli | Sheet: H-Watch_layout.PCBDwf Page 1,2,3 of 3

C:\Users\schuluka\Git\Github\H-Watch\Hardware\H-Watch_V0.2\H-Watch_layout.PCBDwf


Project:

Drawing number: LAY1V0.2 Rev: V0.2 | Format: | Laboratory: ETH_PBL | Sheet: H-Watch_layout.PCBDwf


Project:

Drawing number: LAY1V0.2 Rev: V0.2 | Format: | Laboratory: ETH_PBL | Sheet: H-Watch_layout.PCBDwf

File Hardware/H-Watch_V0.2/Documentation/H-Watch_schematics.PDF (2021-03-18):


Project: H-Watch Main

Drawing number: SCH1V0.2 Rev: V0.2 Date: 11:28:48 | Format: A3 | Laboratory: ETH-PBL Drawn by: schuluka | Sheet: H-Watch.SchDoc Page 1 of 5

C:\Users\schuluka\Git\Github\H-Watch\Hardware\H-Watch_V0.2\H-Watch.SchDoc


Project: H-Watch Sensors

Drawing number: SCH2V0.2 | | Sensors.SchDoc Page 2 of 5

C:\Users\schuluka\Git\Github\H-Watch\Hardware\H-Watch_V0.2\Sensors.SchDoc


Proje c t: H -W a tc h P o we r

Drawing num b e r: SC H 3V 0. 2 R e v : V0. 2 D a te : 1 11:28 : 48 | Form a t: A 3 | Laborato ry : ET H -P B L Drawn by : s chul u k a | Shee t: Power. S c h D o c Pag e 3 of 5

chuluka\Git\Github\H-Watch\H


6 6
7 7

VDD 68

VDDRF 33

VDDSMPS 44
VFBSMPS 41

Project: H-Watch MCH

Drawing number: SCH4V0.2 | | MCU.SchDoc Page 4 of 5

C:\Users\schuluka\Git\Github\H-Watch\Hardware\H-Watch_V0.2\MCU.SchDoc


Proje c t: H -W a tc h N b -I o T

Drawing num b e r: SC H 5V 0. 2 R e v : V0. 2 D a te : 1 11:28 : 48 | Form a t: A 3 | Laborato ry : ET H -P B L Drawn by : s chul u k a | Shee t: BC95-G. S c h D o c Pag e 5 of 5

chuluka\Git\Github\H-Watch\H

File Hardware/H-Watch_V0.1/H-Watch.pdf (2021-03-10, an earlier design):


Project: *

Drawing number: * Rev: * Date: 13:46:07 | Format: A3 | Laboratory: * Drawn by: * | Sheet: H-Watch.SchDoc Page 1 of 5

C:\Users\tommy\OneDrive - Alma Mater Studiorum Università di Bologna\UniBo\SmartCOVID\PrimoPrototipo\SmartWatch\H-Watch.SchDoc


Vdd IO 1

LPS22HB_CS

Project: *

Sensors.SchDoc Page 2 of 5

C:\Users\tommy\OneDrive - Alma Mater Studiorum Università di Bologna\UniBo\SmartCOVID\PrimoPrototipo\SmartWatch\Sensors.SchDoc


C25 CAP 10nF | 2

Projec t : *

Dr awing n u mber : Rev : Da te: | For m a t : | Labor ator y : Dr aw n by : | Sheet : Power .Sc hDoc Page 3 of 5


GND 3

VDD 45
VDD 68

VDDA 14

VDDRF 33

VDDUSB 55

VDDSMPS 44
VFBSMPS 41

Project: *

MCU.SchDoc Page 4 of 5

C:\Users\tommy\OneDrive - Alma Mater Studiorum Università di Bologna\UniBo\SmartCOVID\PrimoPrototipo\SmartWatch\MCU.SchDoc


Projec t : *

Dr awing n u mber : Rev : Da te: | For m a t : | Labor ator y : Dr aw n by : | Sheet : BC95-G .Sch Doc Page 5 of 5

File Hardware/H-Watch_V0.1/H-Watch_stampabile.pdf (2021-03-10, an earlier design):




VOC_SAMP 3 VBAT_OV 7 VRDIV 8 OK_HYST 10 OK_PROG 11 VBAT 18 VSTOR 19 VOUT_SET 12

MCU_LED0; Top; Bottom


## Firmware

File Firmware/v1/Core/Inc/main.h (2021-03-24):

/* USER CODE BEGIN Header */
/**
  ******************************************************************************
  * @file           : main.h
  * @brief          : Header for main.c file.
  *                   This file contains the common defines of the application.
  ******************************************************************************
  * @attention
  *
  * <h2><center>&copy; Copyright (c) 2020 STMicroelectronics.
  * All rights reserved.</center></h2>
  *
  * This software component is licensed by ST under Ultimate Liberty license
  * SLA0044, the "License"; You may not use this file except in compliance with
  * the License. You may obtain a copy of the License at:
  *                             www.st.com/SLA0044
  *
  ******************************************************************************
  */
/* USER CODE END Header */

/* Define to prevent recursive inclusion -------------------------------------*/
#ifndef __MAIN_H
#define __MAIN_H

#ifdef __cplusplus
extern "C" {
#endif

/* Includes ------------------------------------------------------------------*/
#include "stm32wbxx_hal.h"

/* Private includes ----------------------------------------------------------*/
/* USER CODE BEGIN Includes */

/* USER CODE END Includes */

/* Exported types ------------------------------------------------------------*/
/* USER CODE BEGIN ET */

/* USER CODE END ET */

/* Exported constants --------------------------------------------------------*/
/* USER CODE BEGIN EC */

/* USER CODE END EC */

/* Exported macro ------------------------------------------------------------*/
/* USER CODE BEGIN EM */

/* BACKUP_PRIMASK MUST be implemented at the begining of the funtion
   that implement a critical section
   PRIMASK is saved on STACK and recovered at the end of the funtion
   That way RESTORE_PRIMASK ensures critical sections are maintained even in nested calls...*/
#define BACKUP_PRIMASK()  uint32_t primask_bit1 = __get_PRIMASK()
#define DISABLE_IRQ() __disable_irq()
#define ENABLE_IRQ() __enable_irq()
#define RESTORE_PRIMASK() __set_PRIMASK(primask_bit1)


#define CRITICAL_SECTION_BEGIN( )     uint32_t primask_bit= __get_PRIMASK();\
                                    __disable_irq()
#define CRITICAL_SECTION_END( )   __set_PRIMASK(primask_bit)

/*!
 * \brief Returns the minimum value between a and b
 *
 * \param [IN] a 1st value
 * \param [IN] b 2nd value
 * \retval minValue Minimum value
 */
#define MIN( a, b ) ( ( ( a ) < ( b ) ) ? ( a ) : ( b ) )

/*!
 * \brief Returns the maximum value between a and b
 *
 * \param [IN] a 1st value
 * \param [IN] b 2nd value
 * \retval maxValue Maximum value
 */
#define MAX( a, b ) ( ( ( a ) > ( b ) ) ? ( a ) : ( b ) )

/*!
 * \brief Returns 2 raised to the power of n
 *
 * \param [IN] n power value
 * \retval result of raising 2 to the power n
 */
#define POW2( n ) ( 1 << n )

/* USER CODE END EM */

/* Exported functions prototypes ---------------------------------------------*/
void Error_Handler(void);

/* USER CODE BEGIN EFP */

extern void GLOB_SET_EVT( void* xEventGroup, uint32_t x );
extern void Mngm_DeepSleep_en (uint8_t d);

/* USER CODE END EFP */

/* Private defines -----------------------------------------------------------*/
#define LSM303_INT_MAG_Pin GPIO_PIN_0
#define LSM303_INT_MAG_GPIO_Port GPIOA
#define LSM303_INT_MAG_EXTI_IRQn EXTI0_IRQn
#define LSM303_INT2_Pin GPIO_PIN_2
#define LSM303_INT2_GPIO_Port GPIOA
#define LSM303_INT2_EXTI_IRQn EXTI2_IRQn
#define LSM303_INT1_Pin GPIO_PIN_3
#define LSM303_INT1_GPIO_Port GPIOA
#define LSM303_INT1_EXTI_IRQn EXTI3_IRQn
#define RI_INT_Pin GPIO_PIN_4
#define RI_INT_GPIO_Port GPIOA
#define BC95_Reset_Pin GPIO_PIN_5
#define BC95_Reset_GPIO_Port GPIOA
#define LPS22HB_INT_Pin GPIO_PIN_8
#define LPS22HB_INT_GPIO_Port GPIOA
#define LPS22HB_INT_EXTI_IRQn EXTI9_5_IRQn
#define LPS22HB_CS_Pin GPIO_PIN_2
#define LPS22HB_CS_GPIO_Port GPIOB
#define LSM6DSM_INT2_Pin GPIO_PIN_10
#define LSM6DSM_INT2_GPIO_Port GPIOB
#define LSM6DSM_INT2_EXTI_IRQn EXTI15_10_IRQn
#define LSM6DSM_INT1_Pin GPIO_PIN_11
#define LSM6DSM_INT1_GPIO_Port GPIOB
#define LSM6DSM_INT1_EXTI_IRQn EXTI15_10_IRQn
#define LSM6DSM_CS_Pin GPIO_PIN_1
#define LSM6DSM_CS_GPIO_Port GPIOB
#define LED0_Pin GPIO_PIN_0
#define LED0_GPIO_Port GPIOD
#define PPG_INT_Pin GPIO_PIN_6
#define PPG_INT_GPIO_Port GPIOB
#define PPG_INT_EXTI_IRQn EXTI9_5_IRQn
/* USER CODE BEGIN Private defines */

/* USER CODE END Private defines */

#ifdef __cplusplus
}
#endif

#endif /* __MAIN_H */

/************************ (C) COPYRIGHT STMicroelectronics *****END OF FILE****/

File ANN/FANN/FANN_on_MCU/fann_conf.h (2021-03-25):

#ifndef FANN_FANN_CONF_H_
#define FANN_FANN_CONF_H_

#define SIGMOID_RESULTS_0 1
#define SIGMOID_RESULTS_1 1
#define SIGMOID_RESULTS_2 1
#define SIGMOID_RESULTS_3 1
#define SIGMOID_RESULTS_4 1
#define SIGMOID_RESULTS_5 1
#define SIGMOID_SYMMETRIC_RESULTS_0 -1
#define SIGMOID_SYMMETRIC_RESULTS_1 -1
#define SIGMOID_SYMMETRIC_RESULTS_2 -1
#define SIGMOID_SYMMETRIC_RESULTS_3 1
#define SIGMOID_SYMMETRIC_RESULTS_4 1
#define SIGMOID_SYMMETRIC_RESULTS_5 1
#define SIGMOID_VALUES_0 0
#define SIGMOID_SYMMETRIC_VALUES_0 -2
#define SIGMOID_VALUES_1 0
#define SIGMOID_SYMMETRIC_VALUES_1 -2
#define SIGMOID_VALUES_2 0
#define SIGMOID_SYMMETRIC_VALUES_2 -2
#define SIGMOID_VALUES_3 0
#define SIGMOID_SYMMETRIC_VALUES_3 2
#define SIGMOID_VALUES_4 0
#define SIGMOID_SYMMETRIC_VALUES_4 2
#define SIGMOID_VALUES_5 0
#define SIGMOID_SYMMETRIC_VALUES_5 2

#define NUM_NEURONS 139
#define MULTIPLIER 2
#define DECIMAL_POINT 1
#define NUM_INPUT 90
#define NUM_OUTPUT 3
#define NUM_LAYERS 3
#define CONNECTION_RATE 1.000000


#endif // FANN_FANN_CONF_H_

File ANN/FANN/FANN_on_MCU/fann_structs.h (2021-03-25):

//Copyright (c) 2018 ETH Zurich, Ferdinand von Hagen, Michele Magno, Lukas Cavigelli
#include "fann.h"

#ifndef FANN_FANN_STRUCTS_H_
#define FANN_FANN_STRUCTS_H_

enum fann_activationfunc_enum
{
    FANN_LINEAR = 0,
    FANN_THRESHOLD,
    FANN_THRESHOLD_SYMMETRIC,
    FANN_SIGMOID,
    FANN_SIGMOID_STEPWISE,
    FANN_SIGMOID_SYMMETRIC,
    FANN_SIGMOID_SYMMETRIC_STEPWISE,
    FANN_GAUSSIAN,
    FANN_GAUSSIAN_SYMMETRIC,
    /* Stepwise linear approximation to gaussian.
    * Faster than gaussian but a bit less precise.
    * NOT implemented yet.
    */
    FANN_GAUSSIAN_STEPWISE,
    FANN_ELLIOT,
    FANN_ELLIOT_SYMMETRIC,
    FANN_LINEAR_PIECE,
    FANN_LINEAR_PIECE_SYMMETRIC,
    FANN_SIN_SYMMETRIC,
    FANN_COS_SYMMETRIC,
    FANN_SIN,
    FANN_COS
};

/* Enum: fann_train_enum
    The Training algorithms used when training on <struct fann_train_data> with functions like
    <fann_train_on_data> or <fann_train_on_file>. The incremental training looks alters the weights
    after each time it is presented an input pattern, while batch only alters the weights once after
    it has been presented to all the patterns.

    FANN_TRAIN_INCREMENTAL -  Standard backpropagation algorithm, where the weights are
        updated after each training pattern. This means that the weights are updated many
        times during a single epoch. For this reason some problems, will train very fast with
        this algorithm, while other more advanced problems will not train very well.
    FANN_TRAIN_BATCH -  Standard backpropagation algorithm, where the weights are updated after
        calculating the mean square error for the whole training set. This means that the weights
        are only updated once during a epoch. For this reason some problems, will train slower with
        this algorithm. But since the mean square error is calculated more correctly than in
        incremental training, some problems will reach a better solutions with this algorithm.
    FANN_TRAIN_RPROP - A more advanced batch training algorithm which achieves good results
        for many problems. The RPROP training algorithm is adaptive, and does therefore not
        use the learning_rate. Some other parameters can however be set to change the way the
        RPROP algorithm works, but it is only recommended for users with insight in how the RPROP
        training algorithm works. The RPROP training algorithm is described by
        [Riedmiller and Braun, 1993], but the actual learning algorithm used here is the
        iRPROP- training algorithm which is described by [Igel and Husken, 2000] which
        is an variety of the standard RPROP training algorithm.
    FANN_TRAIN_QUICKPROP - A more advanced batch training algorithm which achieves good results
        for many problems. The quickprop training algorithm uses the learning_rate parameter
        along with other more advanced parameters, but it is only recommended to change these
        advanced parameters, for users with insight in how the quickprop training algorithm works.
        The quickprop training algorithm is described by [Fahlman, 1988].

    See also:
        <fann_set_training_algorithm>, <fann_get_training_algorithm>
*/
enum fann_train_enum
{
    FANN_TRAIN_INCREMENTAL = 0,
    FANN_TRAIN_BATCH,
    FANN_TRAIN_RPROP,
    FANN_TRAIN_QUICKPROP,
    FANN_TRAIN_SARPROP
};

/* Enum: fann_stopfunc_enum
    Stop criteria used during training.

    FANN_STOPFUNC_MSE - Stop criteria is Mean Square Error (MSE) value.
    FANN_STOPFUNC_BIT - Stop criteria is number of bits that fail. The number of bits; means the
        number of output neurons which differ more than the bit fail limit
        (see <fann_get_bit_fail_limit>, <fann_set_bit_fail_limit>).
        The bits are counted in all of the training data, so this number can be higher than
        the number of training data.

    See also:
        <fann_set_train_stop_function>, <fann_get_train_stop_function>
*/
enum fann_stopfunc_enum
{
    FANN_STOPFUNC_MSE = 0,
    FANN_STOPFUNC_BIT
};

/* Enum: fann_errorfunc_enum
    Error function used during training.

    FANN_ERRORFUNC_LINEAR - Standard linear error function.
    FANN_ERRORFUNC_TANH - Tanh error function, usually better
        but can require a lower learning rate. This error function agressively targets outputs that
        differ much from the desired, while not targetting outputs that only differ a little that much.
        This activation function is not recommended for cascade training and incremental training.

    See also:
        <fann_set_train_error_function>, <fann_get_train_error_function>
*/
enum fann_errorfunc_enum
{
    FANN_ERRORFUNC_LINEAR = 0,
    FANN_ERRORFUNC_TANH
};

enum fann_nettype_enum
{
    FANN_NETTYPE_LAYER = 0, /* Each layer only has connections to the next layer */
    FANN_NETTYPE_SHORTCUT /* Each layer has connections to all following layers */
};

/* Enum: fann_errno_enum
    Used to define error events on <struct fann> and <struct fann_train_data>.

    See also:
        <fann_get_errno>, <fann_reset_errno>, <fann_get_errstr>

    FANN_E_NO_ERROR - No error
    FANN_E_CANT_OPEN_CONFIG_R - Unable to open configuration file for reading
    FANN_E_CANT_OPEN_CONFIG_W - Unable to open configuration file for writing
    FANN_E_WRONG_CONFIG_VERSION - Wrong version of configuration file
    FANN_E_CANT_READ_CONFIG - Error reading info from configuration file
    FANN_E_CANT_READ_NEURON - Error reading neuron info from configuration file
    FANN_E_CANT_READ_CONNECTIONS - Error reading connections from configuration file
    FANN_E_WRONG_NUM_CONNECTIONS - Number of connections not equal to the number expected
    FANN_E_CANT_OPEN_TD_W - Unable to open train data file for writing
    FANN_E_CANT_OPEN_TD_R - Unable to open train data file for reading
    FANN_E_CANT_READ_TD - Error reading training data from file
    FANN_E_CANT_ALLOCATE_MEM - Unable to allocate memory
    FANN_E_CANT_TRAIN_ACTIVATION - Unable to train with the selected activation function
    FANN_E_CANT_USE_ACTIVATION - Unable to use the selected activation function
    FANN_E_TRAIN_DATA_MISMATCH - Irreconcilable differences between two <struct fann_train_data> structures
    FANN_E_CANT_USE_TRAIN_ALG - Unable to use the selected training algorithm
    FANN_E_TRAIN_DATA_SUBSET - Trying to take subset which is not within the training set
    FANN_E_INDEX_OUT_OF_BOUND - Index is out of bound
    FANN_E_SCALE_NOT_PRESENT - Scaling parameters not present
    FANN_E_INPUT_NO_MATCH - The number of input neurons in the ann and data don't match
    FANN_E_OUTPUT_NO_MATCH - The number of output neurons in the ann and data don't match
*/
enum fann_errno_enum
{
    FANN_E_NO_ERROR = 0,
    FANN_E_CANT_OPEN_CONFIG_R,
    FANN_E_CANT_OPEN_CONFIG_W,
    FANN_E_WRONG_CONFIG_VERSION,
    FANN_E_CANT_READ_CONFIG,
    FANN_E_CANT_READ_NEURON,
    FANN_E_CANT_READ_CONNECTIONS,
    FANN_E_WRONG_NUM_CONNECTIONS,
    FANN_E_CANT_OPEN_TD_W,
    FANN_E_CANT_OPEN_TD_R,
    FANN_E_CANT_READ_TD,
    FANN_E_CANT_ALLOCATE_MEM,
    FANN_E_CANT_TRAIN_ACTIVATION,
    FANN_E_CANT_USE_ACTIVATION,
    FANN_E_TRAIN_DATA_MISMATCH,
    FANN_E_CANT_USE_TRAIN_ALG,
    FANN_E_TRAIN_DATA_SUBSET,
    FANN_E_INDEX_OUT_OF_BOUND,
    FANN_E_SCALE_NOT_PRESENT,
    FANN_E_INPUT_NO_MATCH,
    FANN_E_OUTPUT_NO_MATCH
};
 
typedef struct
{
    int first_connection;
    int last_connection;
    fann_type activation_steepness;
    enum fann_activationfunc_enum activation_function;
} fann_neuron;

typedef struct
{
    int first_neuron;
    int last_neuron;
} fann_layer;

#define fann_max(x, y) (((x) > (y)) ? (x) : (y))
#define fann_min(x, y) (((x) < (y)) ? (x) : (y))
#define fann_safe_free(x) {if(x) { free(x); x = NULL; }}
#define fann_clip(x, lo, hi) (((x) < (lo)) ? (lo) : (((x) > (hi)) ? (hi) : (x)))
#define fann_exp2(x) exp(0.69314718055994530942f*(x))
/*#define fann_clip(x, lo, hi) (x)*/

#define fann_rand(min_value, max_value) (((float)(min_value))+(((float)(max_value)-((float)(min_value)))*rand()/(RAND_MAX+1.0f)))

#ifdef FIXEDFANN

#define fann_mult(x,y) ((x*y) >> DECIMAL_POINT)
#define fann_div(x,y) (((x) << DECIMAL_POINT)/y)
#define fann_random_weight() (fann_type)(fann_rand(0,MULTIPLIER/10))
#define fann_random_bias_weight() (fann_type)(fann_rand((0-MULTIPLIER)/10,MULTIPLIER/10))

#else

#define fann_mult(x,y) (x*y)
#define fann_div(x,y) (x/y)
#define fann_random_weight() (fann_rand(-0.1f,0.1f))
#define fann_random_bias_weight() (fann_rand(-0.1f,0.1f))

#include <math.h>
//#include <arm_math.h>
/* Implementation of the activation functions
 */

/* stepwise linear functions used for some of the activation functions */

/* defines used for the stepwise linear functions */

#define fann_linear_func(v1, r1, v2, r2, sum) (((((r2)-(r1)) * ((sum)-(v1)))/((v2)-(v1))) + (r1))
#define fann_stepwise(v1, v2, v3, v4, v5, v6, r1, r2, r3, r4, r5, r6, min, max, sum) (sum < v5 ? (sum < v3 ? (sum < v2 ? (sum < v1 ? min : fann_linear_func(v1, r1, v2, r2, sum)) : fann_linear_func(v2, r2, v3, r3, sum)) : (sum < v4 ? fann_linear_func(v3, r3, v4, r4, sum) : fann_linear_func(v4, r4, v5, r5, sum))) : (sum < v6 ? fann_linear_func(v5, r5, v6, r6, sum) : max))

/* FANN_LINEAR */
/* #define fann_linear(steepness, sum) fann_mult(steepness, sum) */
#define fann_linear_derive(steepness, value) (steepness)
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

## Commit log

2021-03-10 - HW cad and production
    [BC95-G.SchDoc, H-Watch.GBL, H-Watch.GBO, H-Watch.GBS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]
2021-03-18 opened new H-Watch version V0.2
    [BC95-G.SchDoc, H-Watch.GBL, H-Watch.GBO, H-Watch.GBS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]
2021-03-18 Updated schematics and draftsmans
    [BC95-G.SchDoc, H-Watch.PrjPcb, H-Watch.SchDoc, MCU.SchDoc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]
